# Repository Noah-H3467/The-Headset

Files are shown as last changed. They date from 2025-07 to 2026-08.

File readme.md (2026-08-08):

#  The Headset

"The Headset" is a prototype control system for a wearable headset built around an Arduino Nano Every. The goal is to coordinate physical hardware behavior on the microcontroller at the tap of buttons that are wired to the board, in order to automate the application of a cold compress on the wearer's eyes for the goal of treating eye itching and pain caused by allergies.

I am working on this 'automated allergy icer' because each spring, I repeatedly find myself holding a cold washcloth to my eyes to fight off the pain that comes with my allergies. So my goal was to “automate” the washcloth: I wanted a hands-free way to apply and maintain a cold compress on one or both eyes. The prototype has achieved this key functionality, but is in need of refinement.
- There are currently three buttons. The first two toggle the left and right "arms" up and down. At the end of each arm is a small cold pack attached to it. The third button is an Emergency Stop button, cutting output to the motors.

## Navigation
- This is a PlatformIO project, allowing for easier development in VSCode as opposed to the Arduino IDE.
- The `src` folder contains the code in C++ for the allergy icer. The `include` and `lib` folders may contain other code files in the future as I change the code structure.
- The `CAD` folder contains all cad related things. Parts will contain stl files for 3d printed parts and drawings will contain part and assembly drawings.
- Documentation will contain the initial BOM and an updated one for future iterations, as well as other notes I have made about this project.

## Hardware Control In The Sketch
The C++ source code is structured as a small embedded control loop rather than a collection of one-off callbacks. In `sketch/main.cpp`, the firmware keeps the live hardware state in a few shared variables (arm state, emergency stop enabled) and updates them through handlers called by `checkButtons()`. Those handlers are intentionally lightweight, while the `updateSetpoints()` function, also called by the `periodic()` loop, is responsible for quickly applying that state to the hardware.

The supporting C++ files reinforce the split between main logic and hardware-managing code: 
- Pin mapping and board-specific constants live in `src/Constants.hpp`
- Button handling is wrapped in `DigitalInput` for debouncing and edge detection
- Temperature sensing is isolated in `Thermometer` so the main sketch can treat sensing as a service rather than embedding hardware details inline. 

This way, the firmware can keep safety-sensitive behavior local to the microcontroller and avoid relying on web requests for timing.

Motor control is still in progress, but the architecture already has the intended structure: `main.cpp` computes desired setpoints from the current arm state, and the lower-level DCMotor.hpp consumes those setpoints once it is fully wired up.

## How to Use
- Use the resources in this repository to obtain the materials necessary to build the headset. Either clone this repository or specifically download the STL files to print the custom parts.
 - Note: As the current CAD version is still under refinement, it is not uploaded to the CAD folder yet.
- Download the Arduino IDE and copy the code into a `.ino` file. If you didn't clone the repository, make sure that `TheHeadset.ino` is inside a folder calledd "TheHeadset" to use in the Arduino IDE. 
- Or use the PlatformIO extension in your IDE (like VSCode), clone the repo, and open this Arduino project there.

## Current and Future Plans (in this project's Github Issues)
I intend to make improvements for this prototype and turn it into a refined product. I still intend to stay open source. Future iterations will:
- Use a more compact microcontroller - Arduino Nano Every - and design a custom PCB to lighten the design in order to improve user comfortability.
- Large modifications to the frame to improve appearance and user comfortability.
- Improve consistency of arm subsystems by switching to a different DC motor with a custom-designed gearbox.
- Create a better way of informing the user that a cold pack has warmed: I will likely use LEDs or a buzzer for this purpose.
- Introduce a self-refrigeration mechanism to increase time between cold pack replacing. This enhancement may feature ice cubes or refrigerant.
 - This is a long-term improvement, something to attempt once the others are successfully completed.

## License
This program is free software: you can redistribute it and/or modify it under the terms of the GNU General Public License as published by the Free Software Foundation, either version 3 of the License, or any later version.

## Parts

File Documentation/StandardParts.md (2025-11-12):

# Standard Parts
Will contain links to off-the-shelf or common parts used.

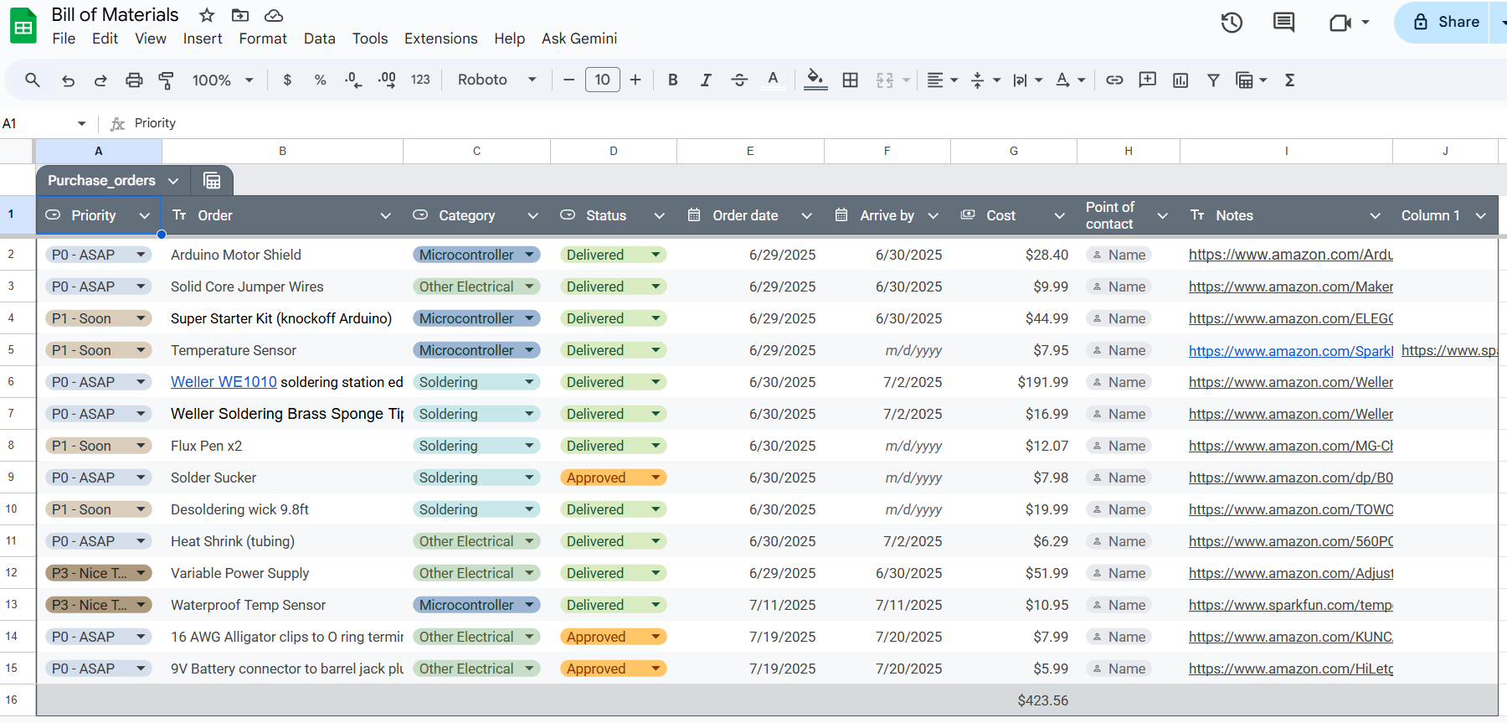
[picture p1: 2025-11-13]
Documentation/Initial Bill of Materials.png

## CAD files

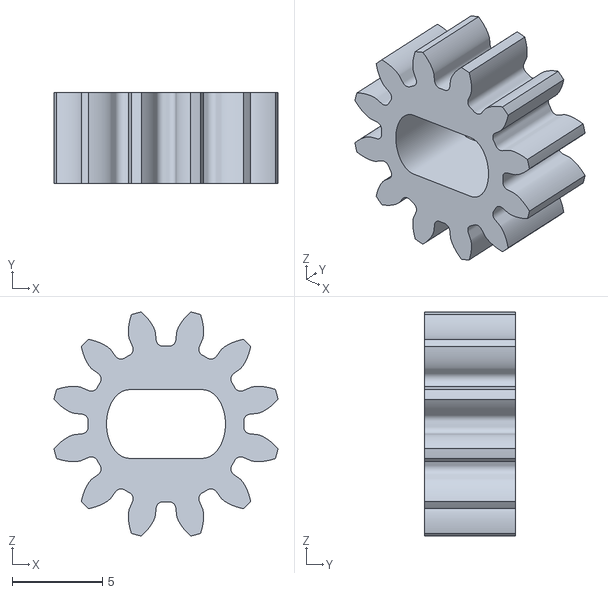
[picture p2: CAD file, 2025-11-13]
CAD/Parts/Gears - Spur gear (12 teeth).stl
12.4 x 5.08 x 12.4

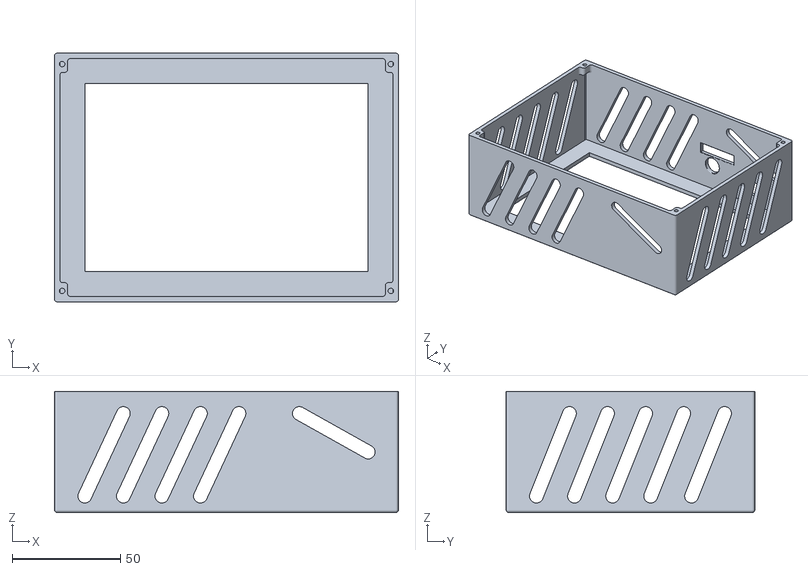
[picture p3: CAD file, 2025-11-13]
CAD/Parts/Controller Housing - Base.stl
158.7 x 114.7 x 55.8

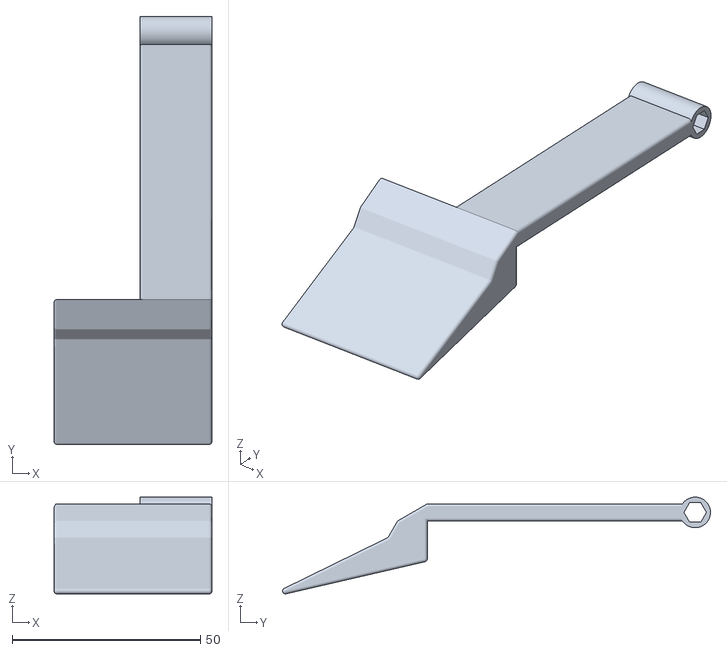
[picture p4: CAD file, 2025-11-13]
CAD/Parts/Arms - Left Arm.stl
41.9 x 113.6 x 25.7

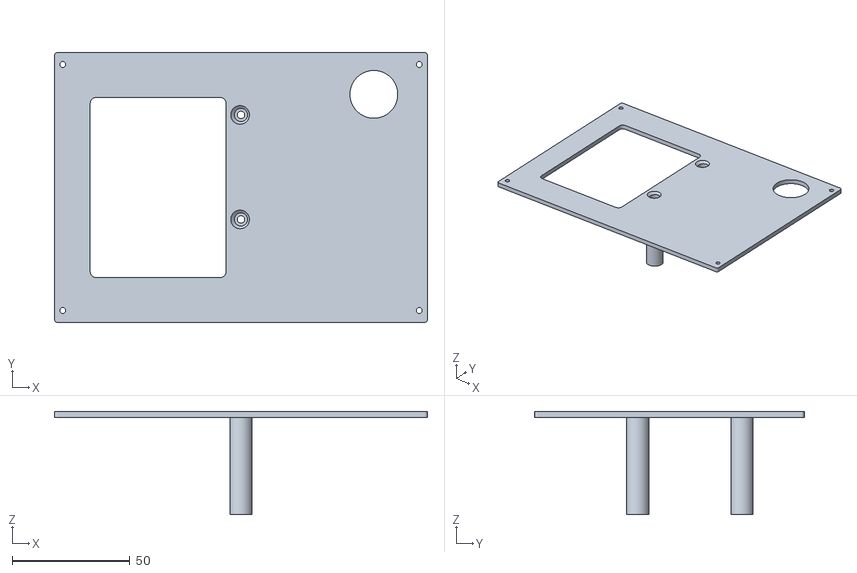
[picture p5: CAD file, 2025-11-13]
CAD/Parts/Controller Housing - Lid.stl
158.7 x 114.7 x 43.9

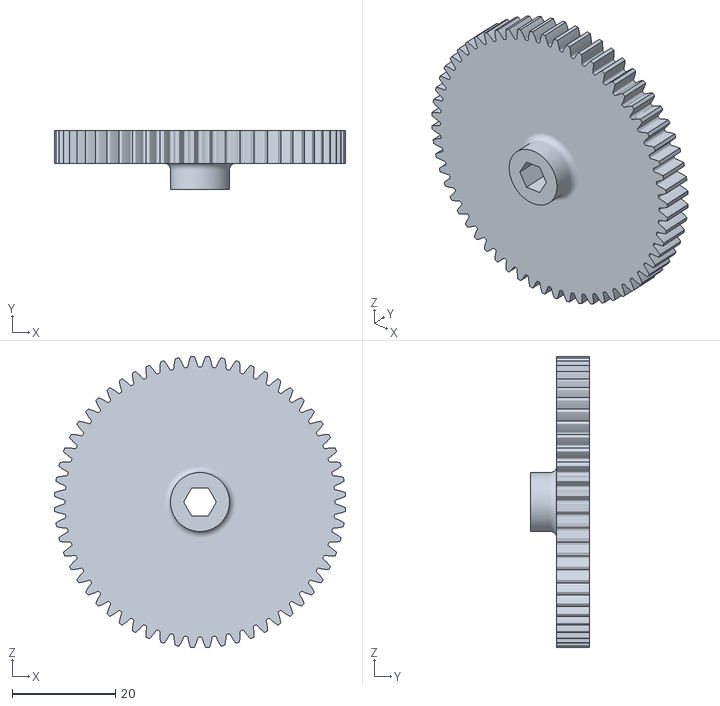
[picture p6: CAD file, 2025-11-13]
CAD/Parts/Gears - Spur gear (60 teeth).stl
56.4 x 11.4 x 56.4

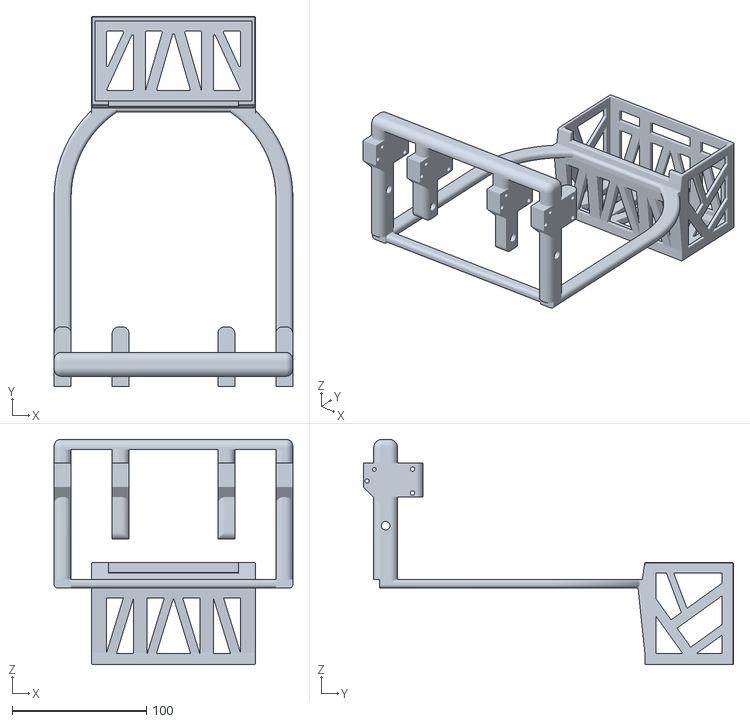
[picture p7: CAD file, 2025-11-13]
CAD/Parts/Headset Frame.stl
177.8 x 275.6 x 167.9

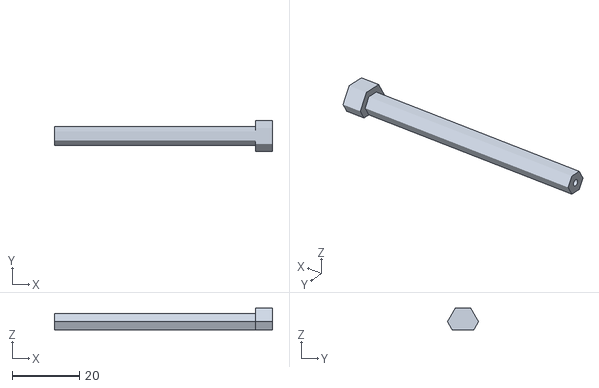
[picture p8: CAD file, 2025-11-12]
CAD/Parts/Axles - Arm Pivot Hex.stl
64.8 x 9.25 x 6.43

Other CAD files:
CAD/Parts/Arms - Right Arm.stl

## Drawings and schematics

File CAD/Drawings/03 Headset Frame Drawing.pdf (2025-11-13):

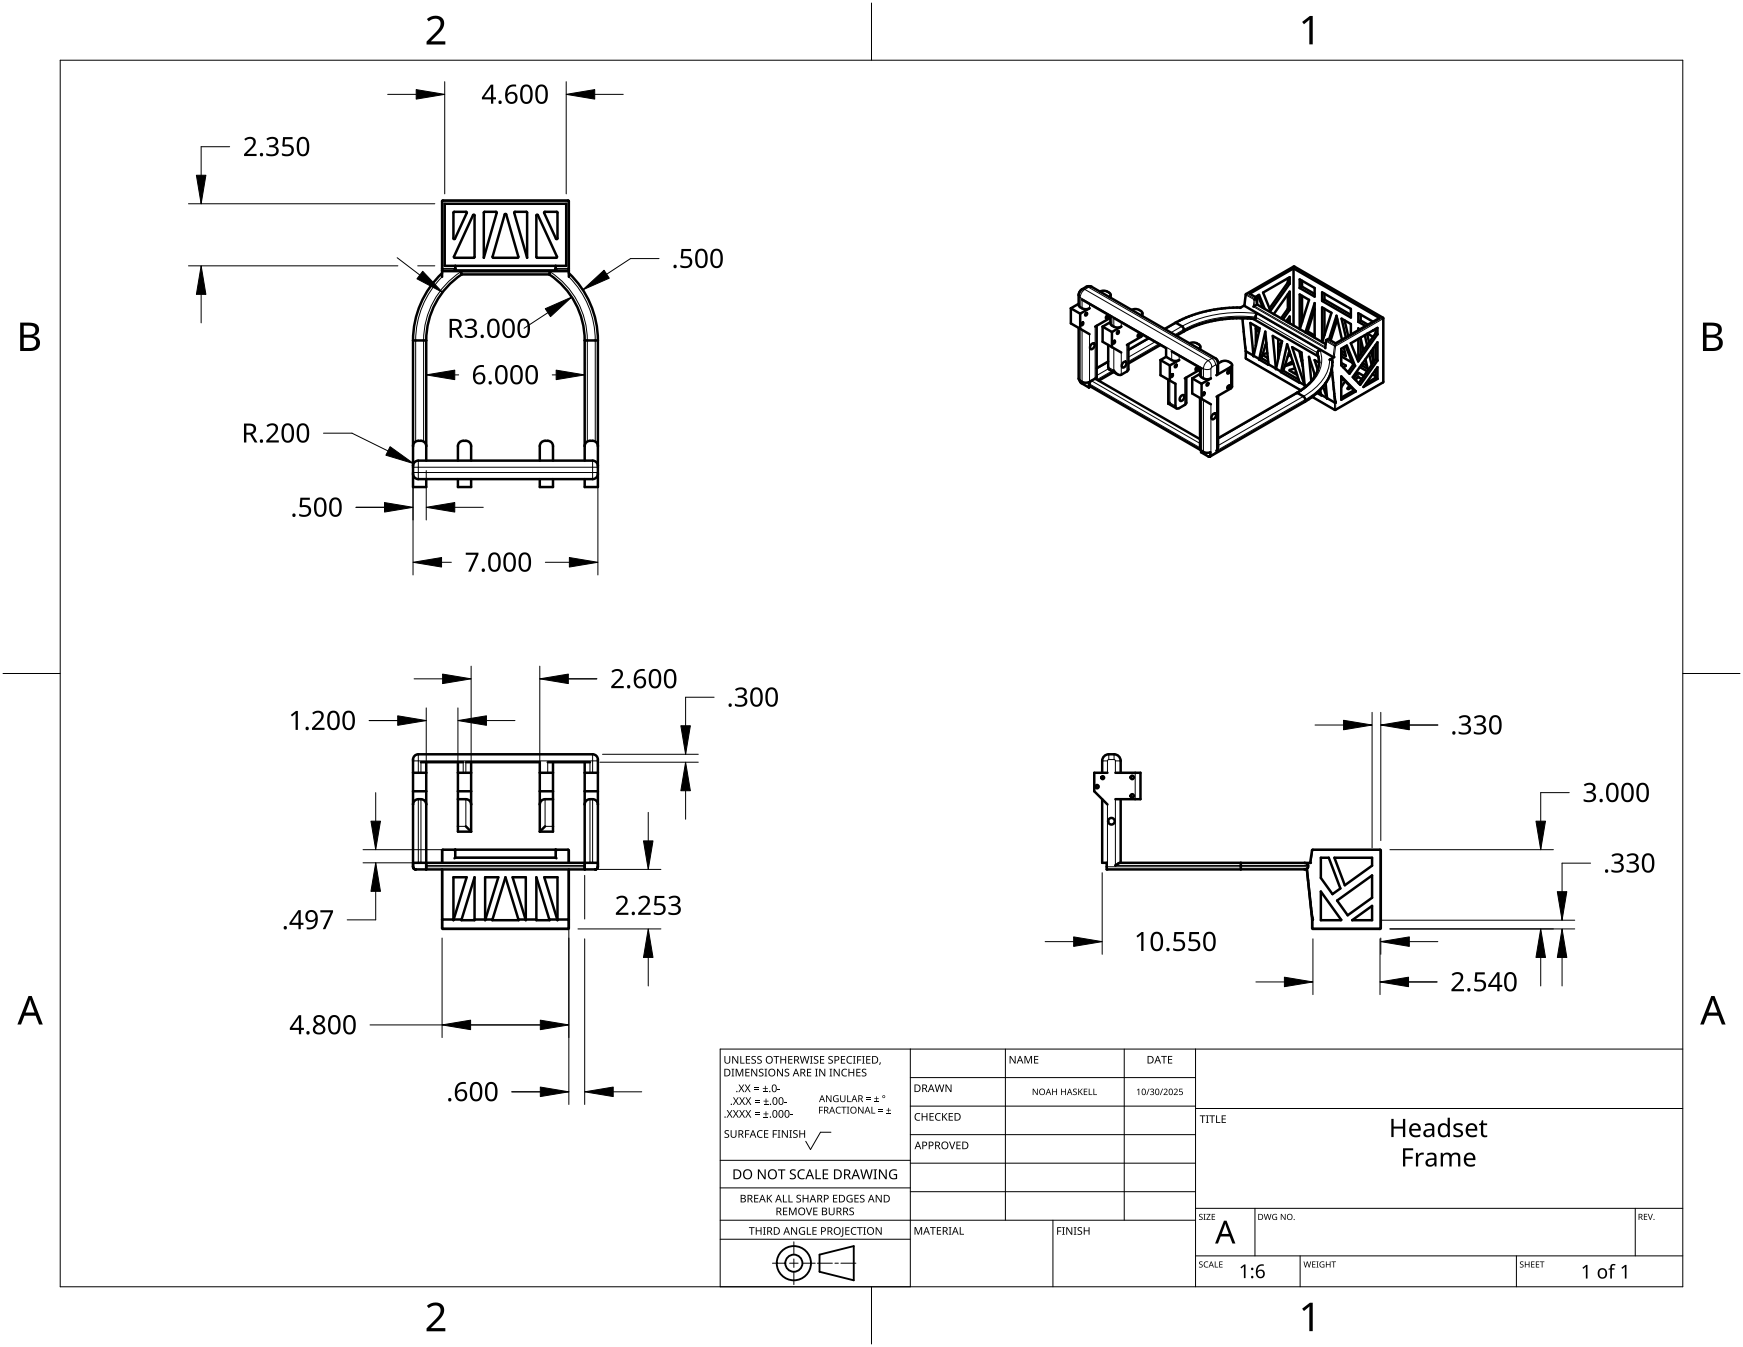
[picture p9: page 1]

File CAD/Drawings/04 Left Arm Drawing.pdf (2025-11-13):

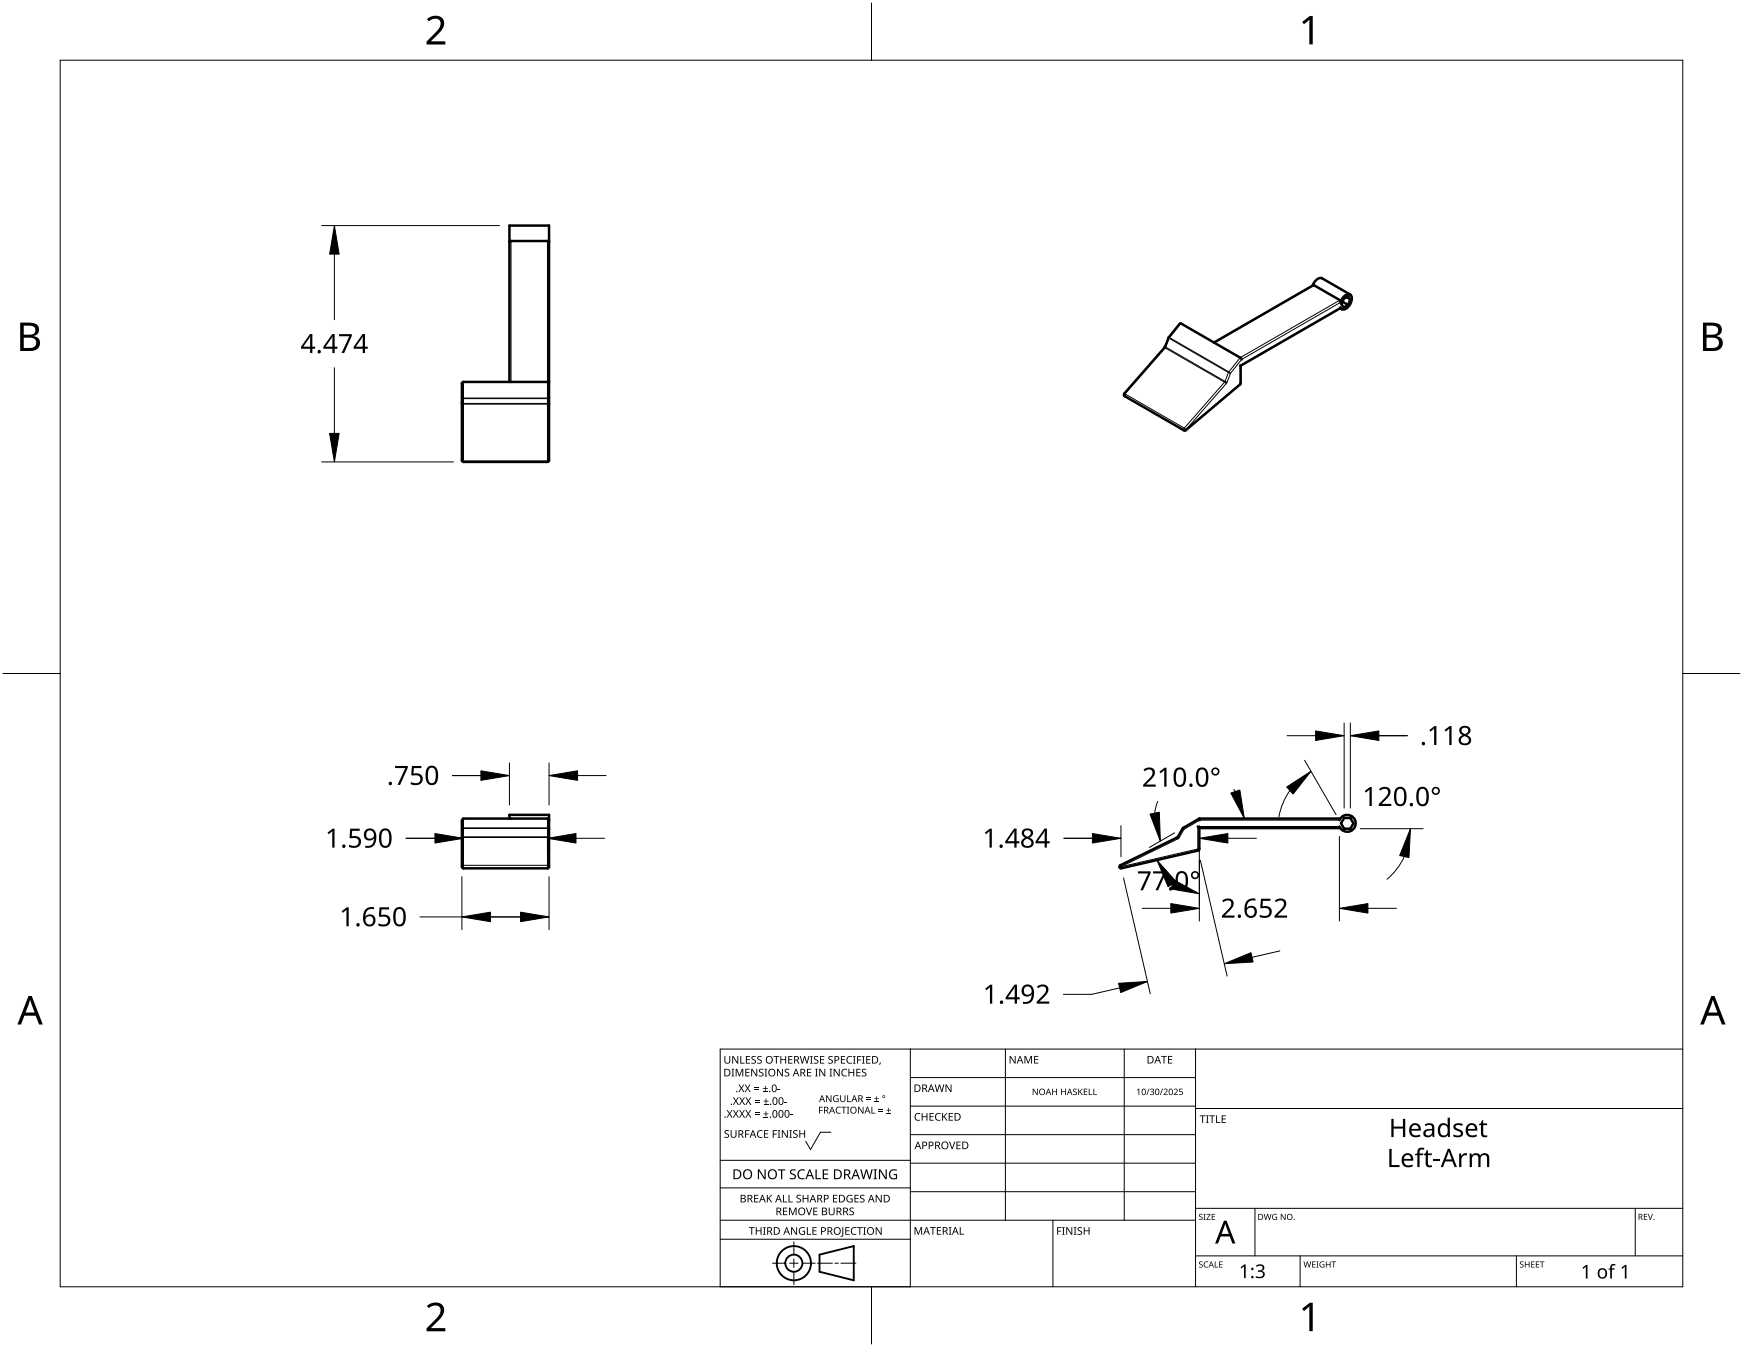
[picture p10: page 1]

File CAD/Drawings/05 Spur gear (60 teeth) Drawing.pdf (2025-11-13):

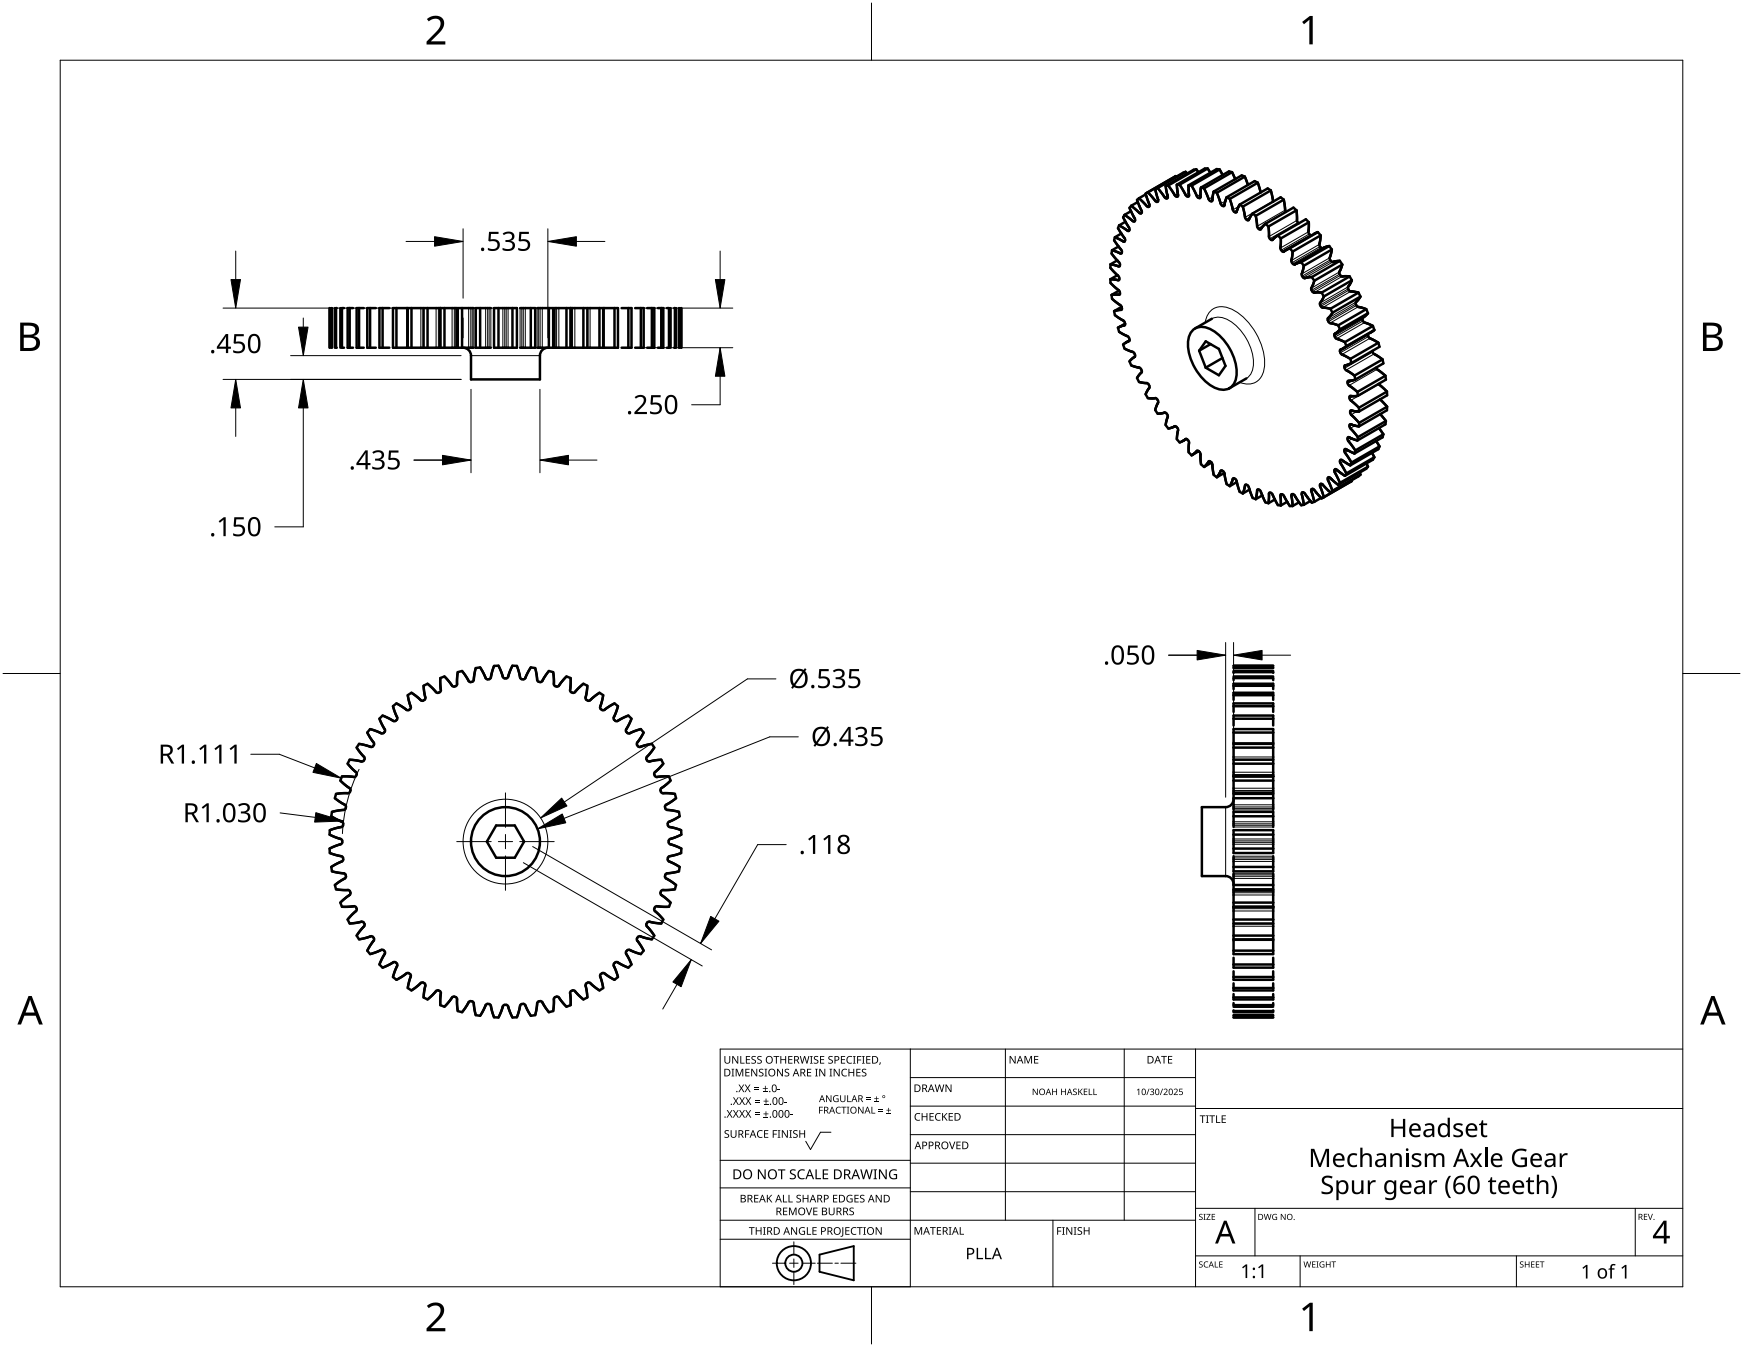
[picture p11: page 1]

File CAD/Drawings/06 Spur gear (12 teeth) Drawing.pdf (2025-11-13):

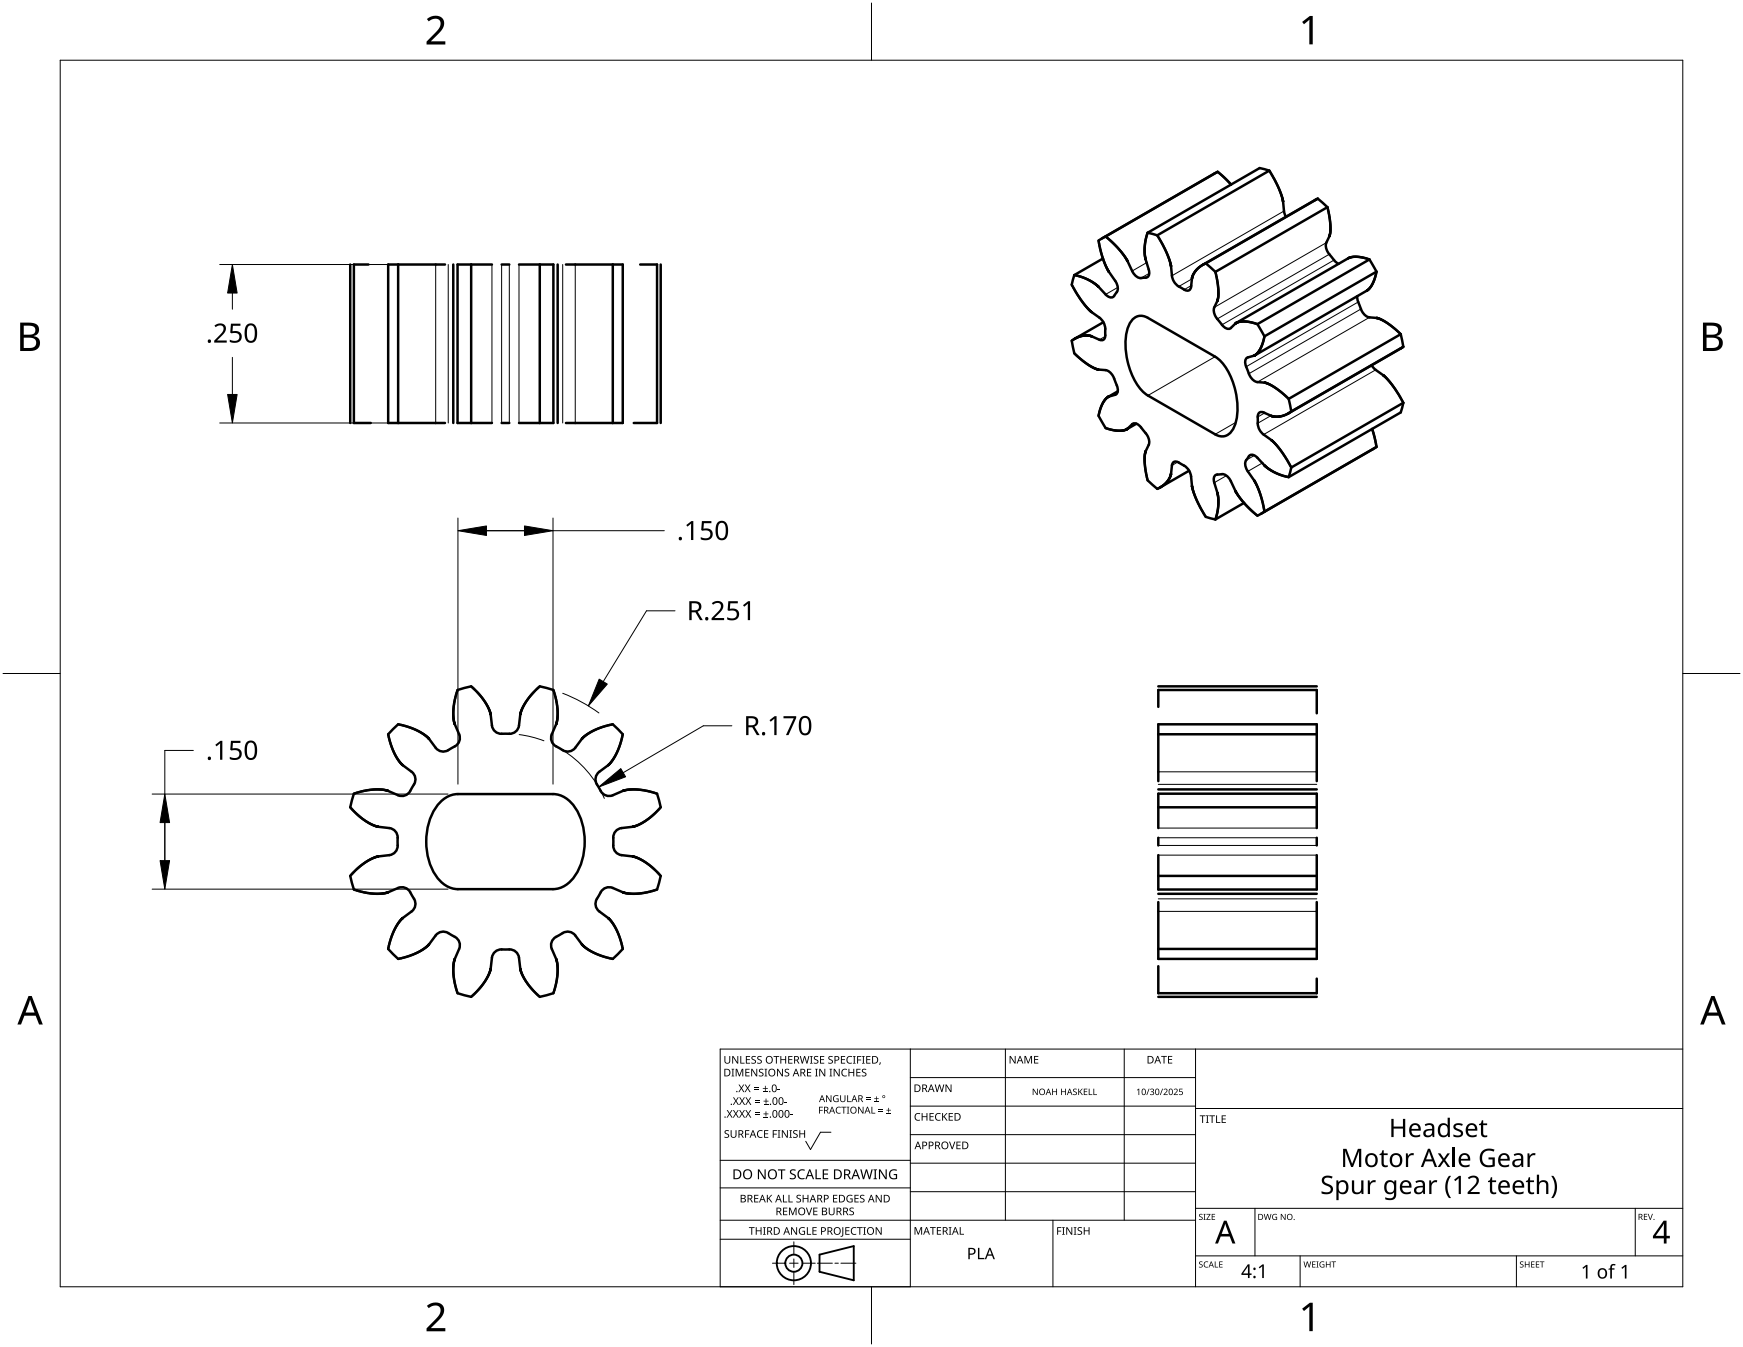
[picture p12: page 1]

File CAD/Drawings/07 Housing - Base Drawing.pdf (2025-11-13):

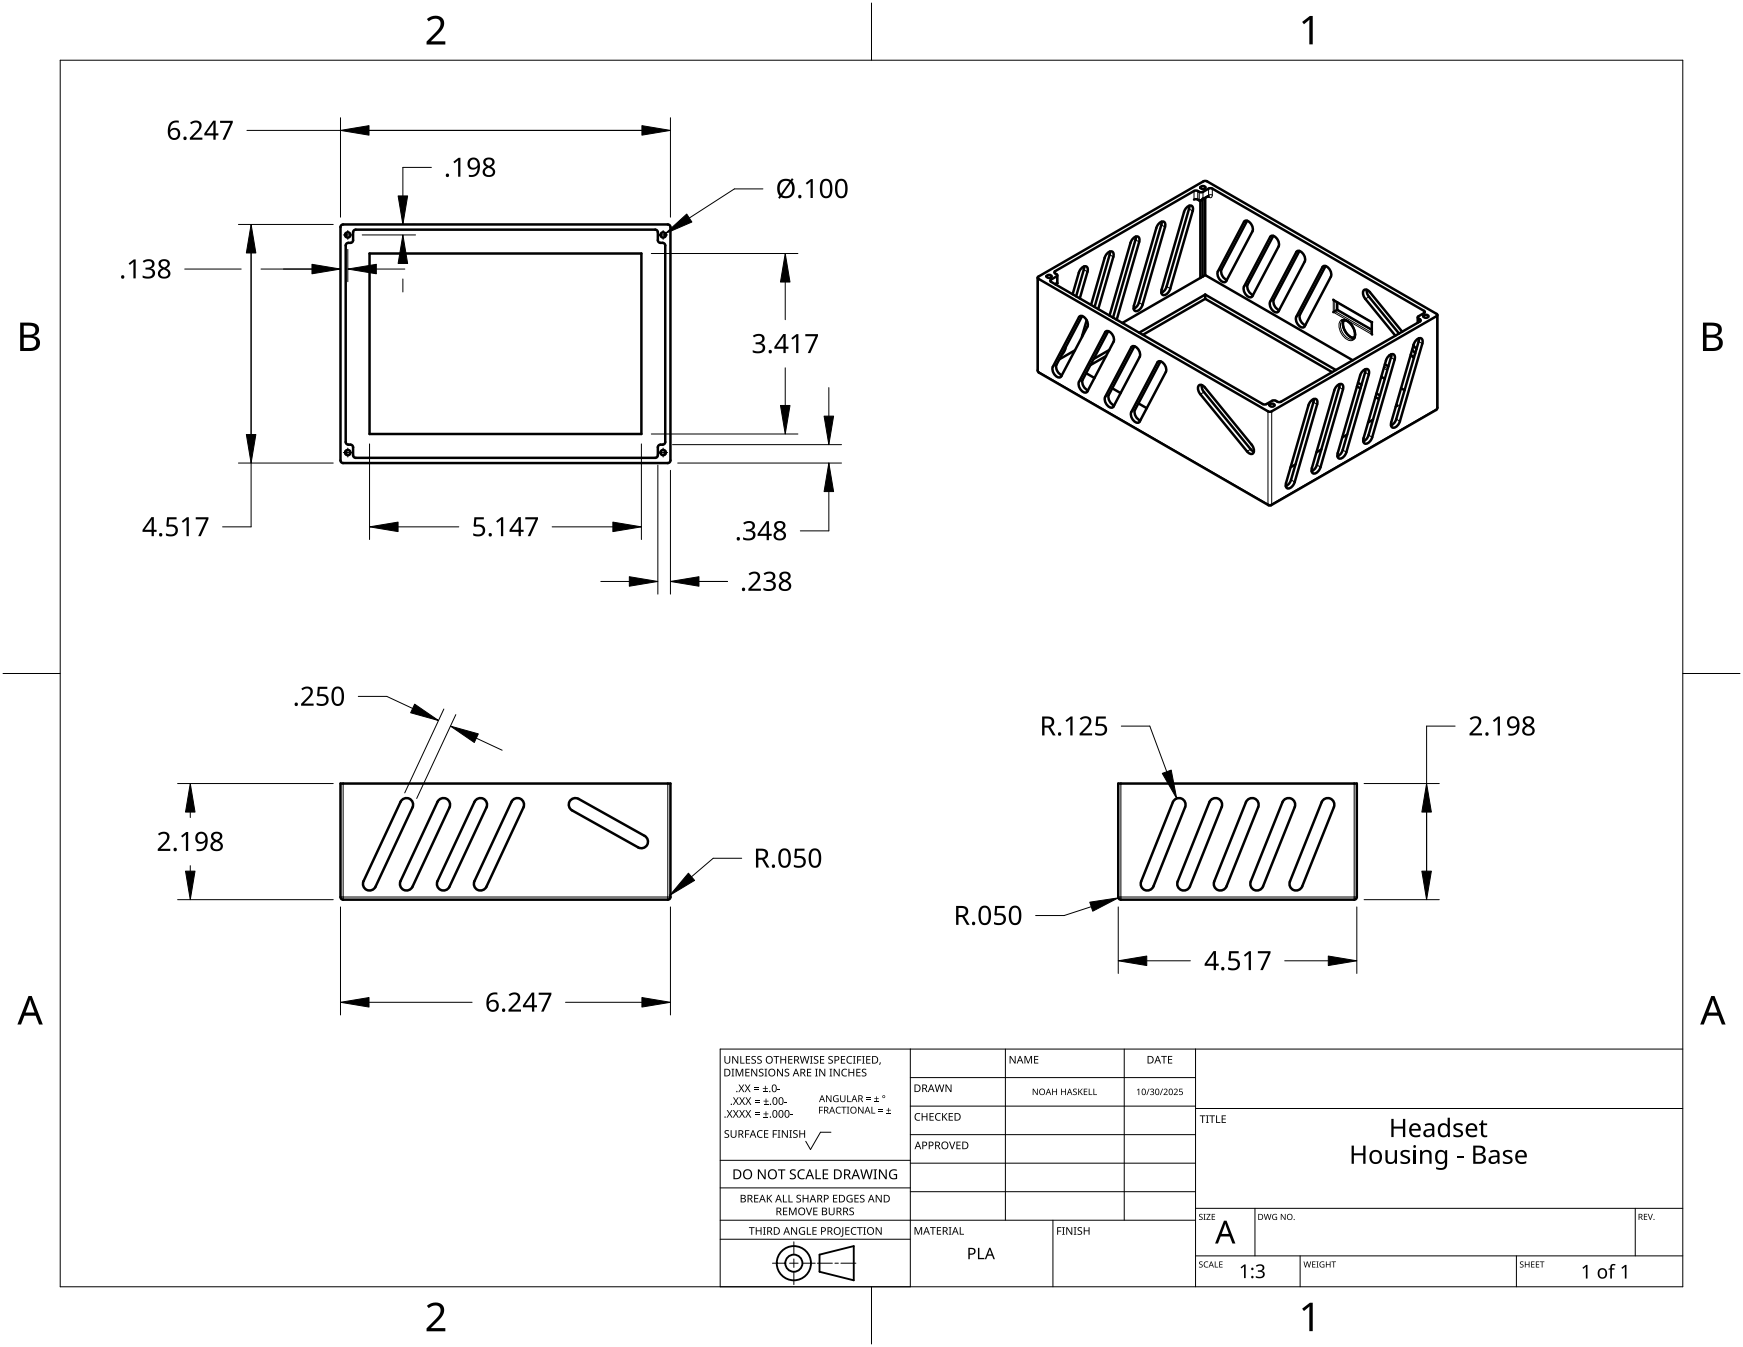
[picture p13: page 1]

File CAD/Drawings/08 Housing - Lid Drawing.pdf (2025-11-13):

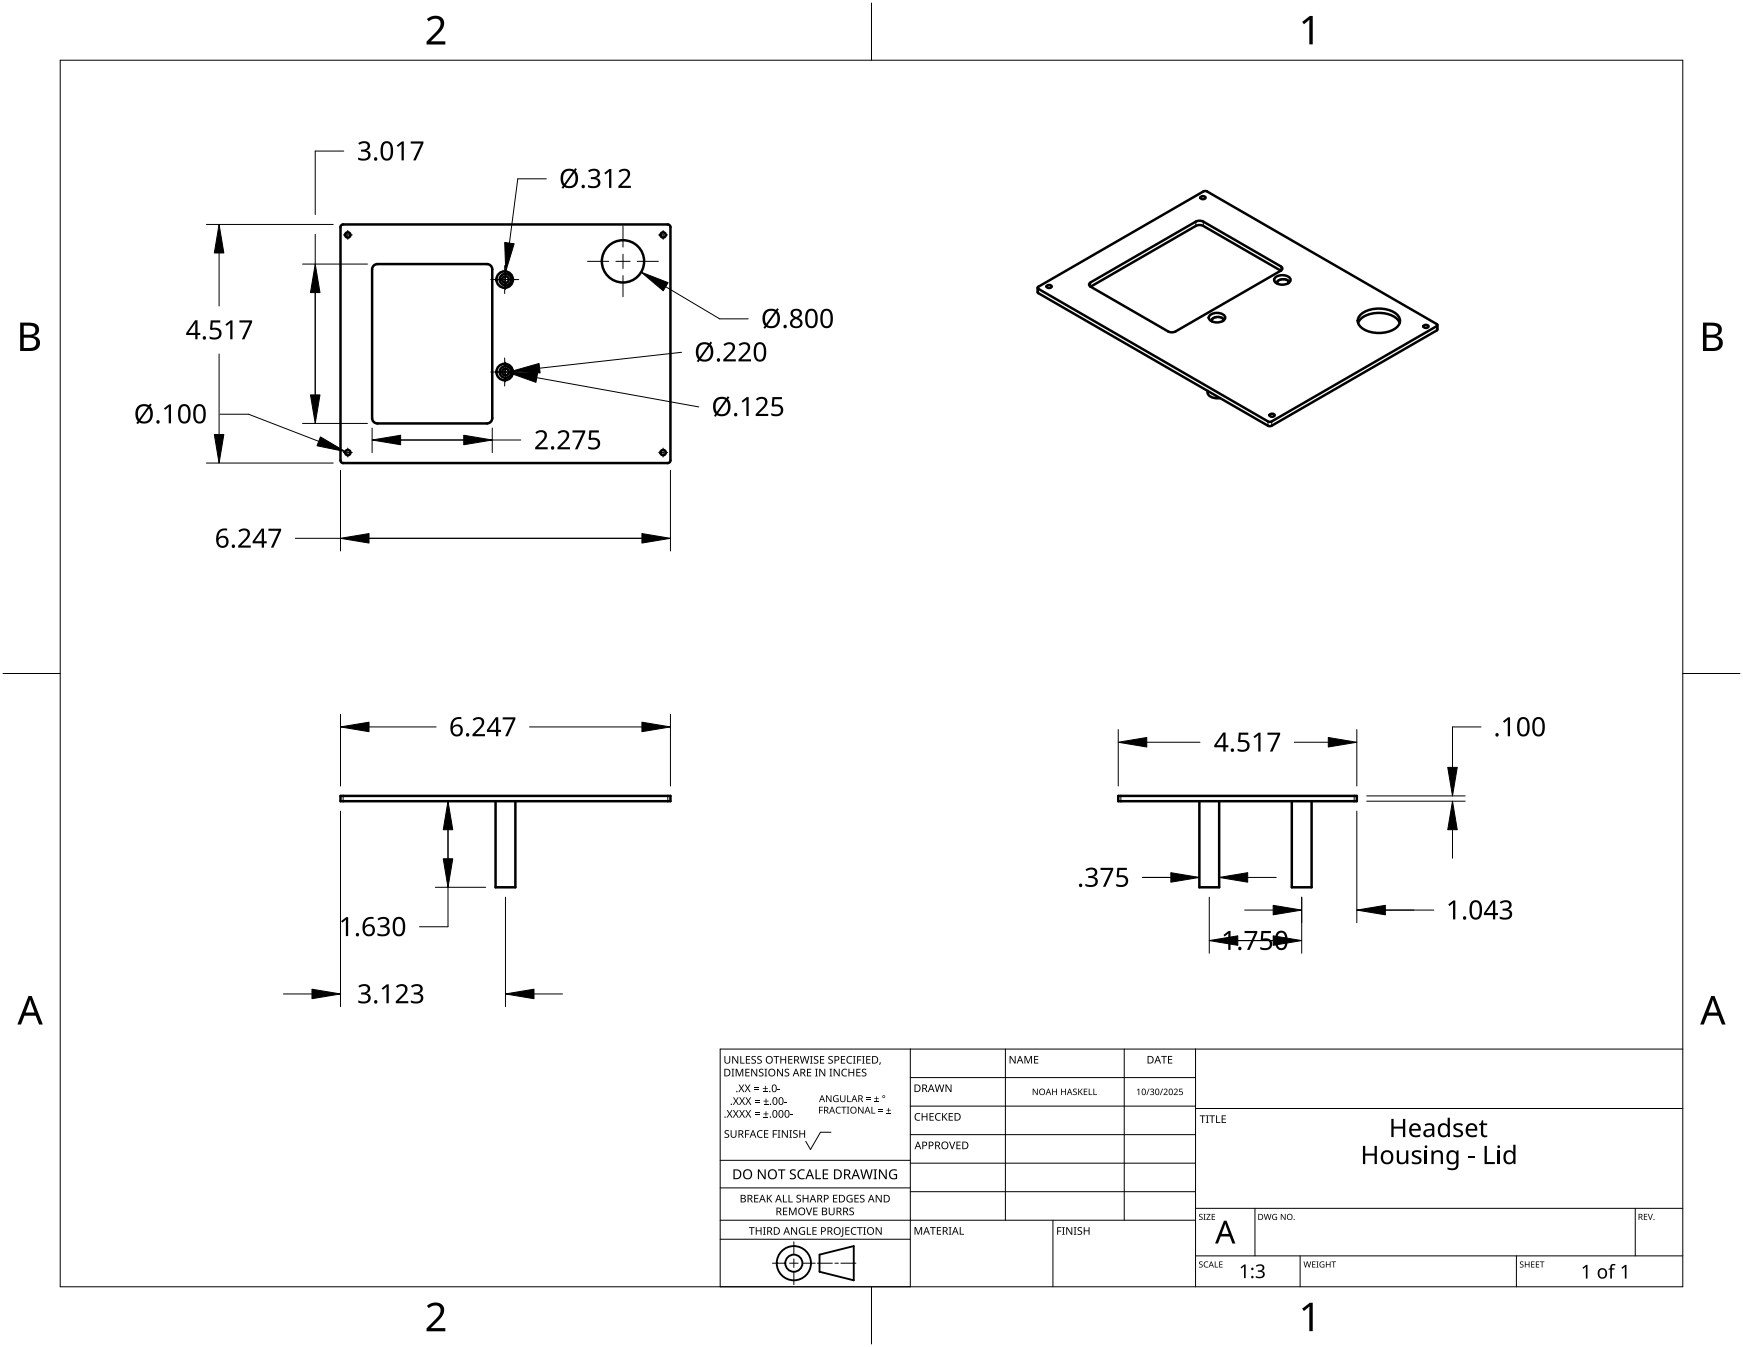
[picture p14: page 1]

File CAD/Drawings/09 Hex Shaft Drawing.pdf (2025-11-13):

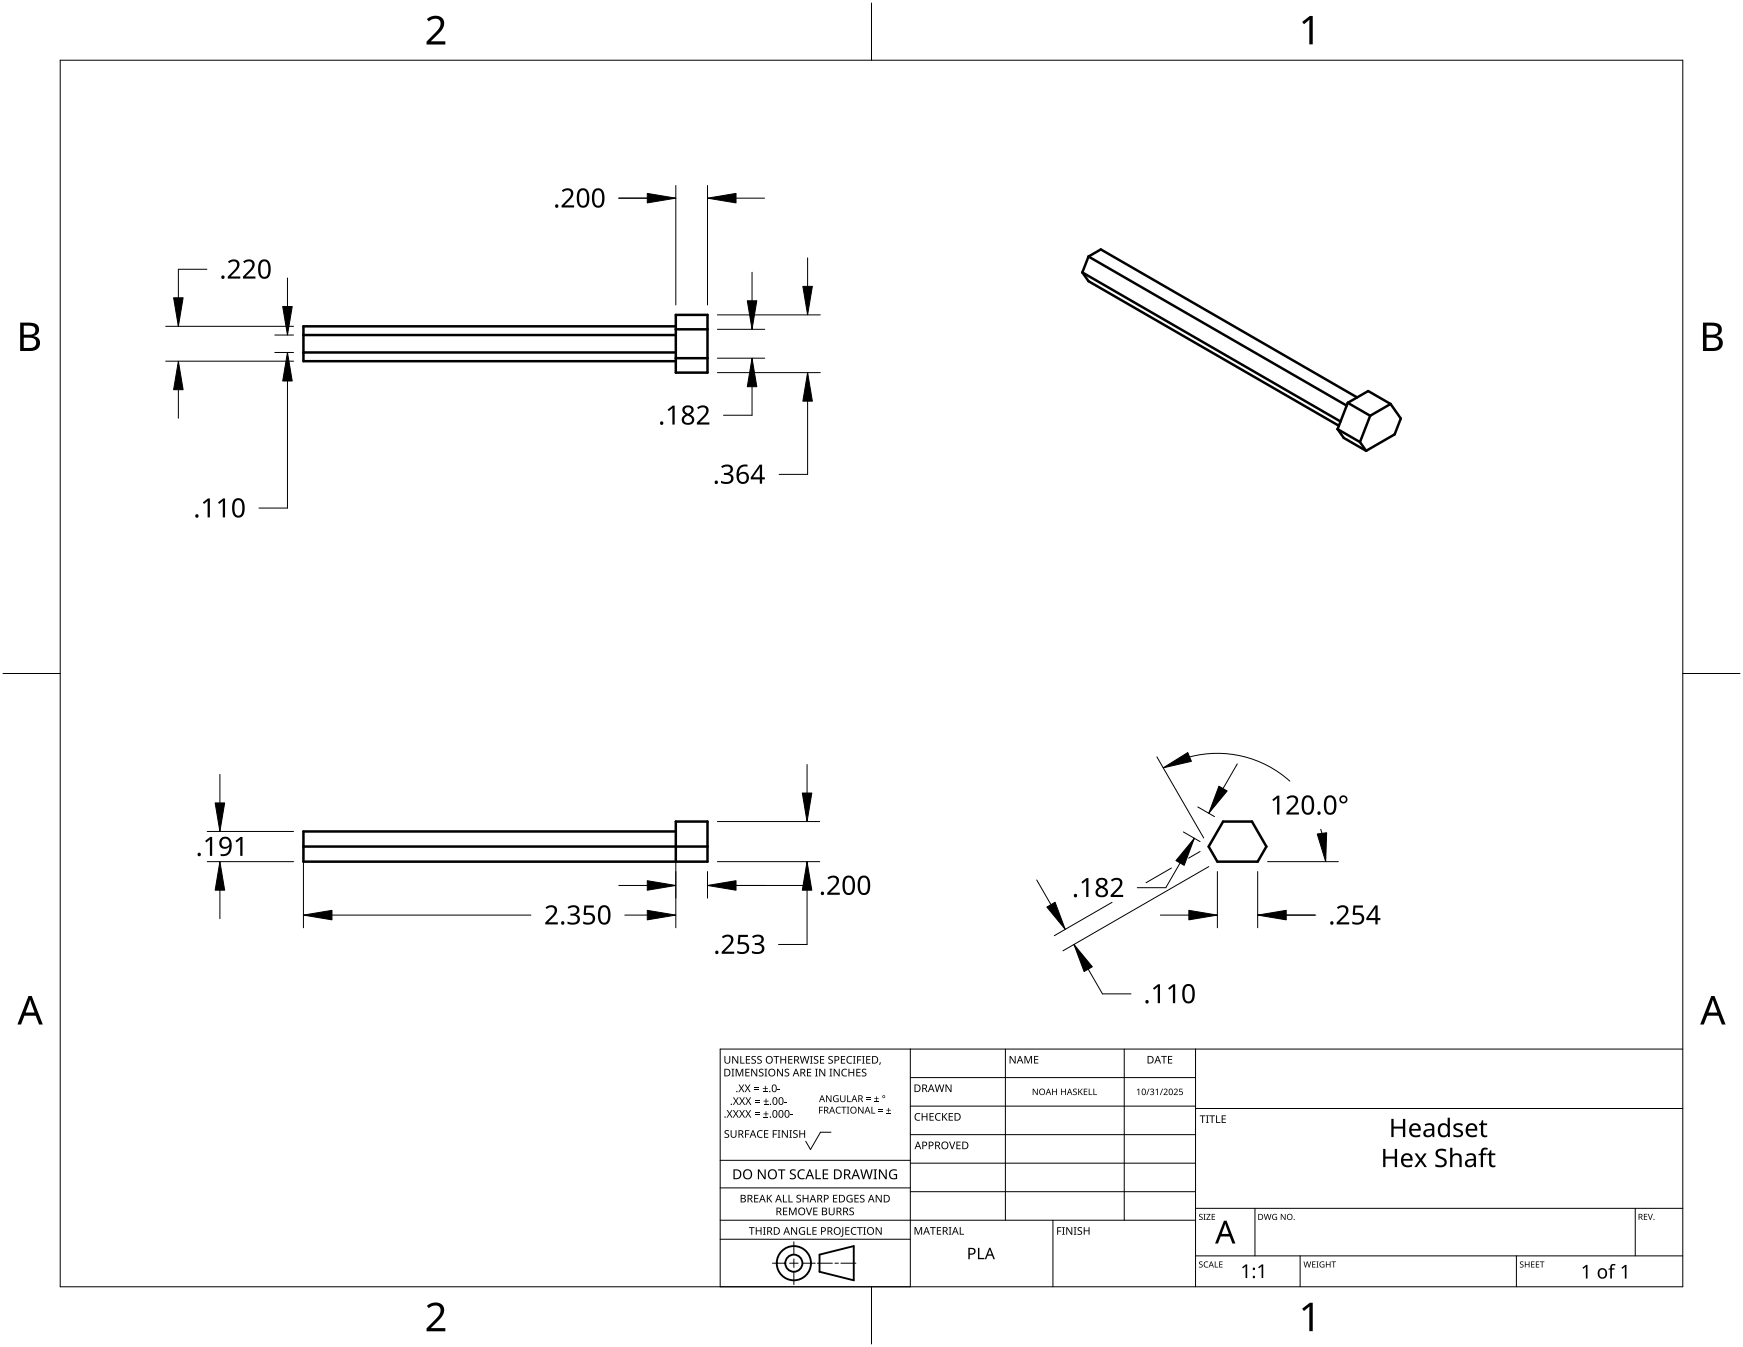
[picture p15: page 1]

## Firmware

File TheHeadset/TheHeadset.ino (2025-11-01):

#include <util/atomic.h>
#include <DallasTemperature.h>
#include <OneWire.h>
#include <QuadratureEncoder.h>

/* Based on a SimplePID class from CurioRes to compute the control signal. 
  I used it out of convenience to familiarize myself with class structure in C++.
  https://github.com/curiores/ArduinoTutorials/blob/main/MultipleEncoders/SimplePositionPID/SimplePositionPID.ino */
class SimplePID{
  private:
    float kp, kd, ki, ks, umax; // Parameters
    float eprev, eintegral; // Storage

  public:
  // Constructor
  SimplePID() : kp(1), kd(0), ki(0), ks(50), umax(255), eprev(0.0), eintegral(0.0){}

  // A function to set the parameters
  void setParams(float kpIn, float kdIn, float kiIn, float ksIn, float umaxIn){
    kp = kpIn; kd = kdIn; ki = kiIn; ks = ksIn; umax = umaxIn;
  }

  // A function to compute the control signal
  void evalu(int value, int target, float deltaT, int &pwr, int &dir){
    // error
    int e = target - value;
  
    // derivative
    float dedt = (e-eprev)/(deltaT);
  
    // integral
    eintegral = eintegral + e*deltaT;

    // control signal
    float u = kp*e + kd*dedt + ki*eintegral;
  
    // motor power
    pwr = (int) fabs(u);
    if( pwr > umax ){
      pwr = umax;
    } else if (pwr < ks) {
      pwr = ks;
    }
  
    // motor direction
    dir = 1;
    if(u>0){
      dir = -1;
    }
  
    // store previous error
    eprev = e;
  }
};

// Define Sensors
#define ONE_WIRE_BUS 4 // Pin # of Sensor 1
#define TWO_WIRE_BUS 10 // Pin # of Sensor 2
OneWire oneWire(ONE_WIRE_BUS);
OneWire twoWire(TWO_WIRE_BUS);
DallasTemperature sensor1(&oneWire); // Left
DallasTemperature sensor2(&twoWire); // Right

// {Right Motor, Left Motor}
const int DIRECTION_PINS[] = {12, 13};
const int PWM_PINS[] = {3, 11};
const int BRAKE_PINS[] = {9, 8};
Encoders firstEncoder(2,5);
Encoders secondEncoder(6,7); // the encoder objects could use analog pins

//boolean to switch motor direction
bool directionState = false;

// Initial target position
const int highPos = 800;
const int lowPos = -50;
int target[] = {highPos, highPos};

// For PID time calculation
long prevT = 0;

// PID class instance list length 2 - number of motors
SimplePID pid[2];
int STATIC_GAIN[] = {255, 73}; // for each motor

// Counter for printing position on the serial
int counter = 0;

// Define button pins
// https://forum.arduino.cc/t/using-analog-pins-for-push-buttons/309407/7
const int leftButton = A0;
const int rightButton = A1;
// Press this to zero the encoders. TODO: Make the press of this button start homing
const int homeButton = A2;
// Records the button state. Either HIGH or LOW.
int leftButtonState = LOW;
int rightButtonState = LOW;
bool homeButtonState = LOW;

void setup() {
  Serial.begin(9600);
  sensor1.begin();
  sensor2.begin();
  
  //define pins
  for (int k = 0; k < 2; k++) {
    // MOTOR
    pinMode(DIRECTION_PINS[k], OUTPUT);
    pinMode(PWM_PINS[k], OUTPUT);
    pinMode(BRAKE_PINS[k], OUTPUT);

    pid[k].setParams(3,0.15,0.0,50,255);
  }

  resetEncoders();
  // Tell Motor #1 to stop
  setMotor(1, DIRECTION_PINS[0], 0.0, PWM_PINS[0]);

  // Initialize the button pins as inputs:
  pinMode(leftButton, INPUT);   
  pinMode(rightButton, INPUT);
  pinMode(homeButton, INPUT);
}

unsigned long lastMilli = 0;
unsigned long lastTempMilli = 0; // To be able to run long temperature stuff that takes a second while checking PID
unsigned long lastTempInProgressMilli = 0;

void loop() {

  /* Request and report temperature ever 30 sec */
  if (millis()-lastTempMilli >= 30000) {
    lastTempMilli = millis();
    requestTemps();
    lastTempInProgressMilli = millis();

    while (millis()-lastTempInProgressMilli < 750) {
      if (millis()-lastMilli > 20) {
        lastMilli = millis();  

        updateButtonState();
        updatePID();
      }
    }
    updateTemperatures();
  }
  if (millis()-lastMilli > 20) {
    lastMilli = millis();  

    updateButtonState();
    updatePID();

  }
}

void requestTemps() {
  // Get temperatures
  sensor1.requestTemperatures();
  sensor2.requestTemperatures();
}

// requestTemps() must be called at least 0.75 seconds before calling this
// Currently gets thermometer reading and prints it to the serial.
void updateTemperatures() {
  Serial.print("Sensor 1: Celsius temperature: ");
  // Why "byIndex"? One can have more than one IC on the same bus. 0 refers to the first IC on the wire
  Serial.print(sensor1.getTempCByIndex(0)); 
  Serial.print(" - Fahrenheit temperature: ");
  Serial.println(sensor1.getTempFByIndex(0));
  Serial.print("Sensor 2: Celsius temperature: ");
  Serial.print(sensor2.getTempCByIndex(0)); 
  Serial.print(" - Fahrenheit temperature: ");
  Serial.println(sensor2.getTempFByIndex(0));

  delay(1000); // Update every second
}

void updatePID() {

  // time difference
  long currT = micros();
  float deltaT = ((float) (currT - prevT))/( 1.0e6 );
  prevT = currT;
  
  lastMilli = millis();  

  long pos[2];
  pos[0] = -firstEncoder.getEncoderCount();
  pos[1] = secondEncoder.getEncoderCount();

  // loop through the motors
  for(int k = 0; k < 2; k++){
    int pwr, dir;
    // evaluate the control signal
    pid[k].evalu(pos[k], target[k], deltaT, pwr, dir);
    // signal the motor
    // Flip direction for Right Arm motor aka the 1st motor
    if (k==0){
      dir *= -1;
      setMotor(dir, DIRECTION_PINS[k], pwr, PWM_PINS[k]);
    } else {
      setMotor(dir, DIRECTION_PINS[k], pwr, PWM_PINS[k]);
    }
  }
  // Print arm information every 10x this function is called
  if (counter % 10 == 0) {
    for(int k = 0; k < 2; k++){
      if (k == 1) {
      Serial.print("                                                     ");
      }
      Serial.print("Target of motor ");
      Serial.print(k+1);
      Serial.print(": ");
      Serial.print(target[k]);
      Serial.print(" ");
      Serial.print("Position of encoder: ");
      Serial.print(pos[k]);
      Serial.println(" ");
    }
  }
  counter++;
}

void resetEncoders() {
  // Through testing, -20 ticks has been more effective than 0
  firstEncoder.setEncoderCount(-20.0);
  secondEncoder.setEncoderCount(-20.0);
}

void setMotor(int dir, int dirPin, int pwmVal, int pwmPin) {
  if (dir==1) {
    digitalWrite(dirPin, HIGH);
    //set work duty for the motor
    analogWrite(pwmPin, pwmVal);
  } else if (dir == -1) {
    digitalWrite(dirPin, LOW);
    //set work duty for the motor
    analogWrite(pwmPin, pwmVal);
  } else {
    analogWrite(pwmPin, 0);
  }
}

void updateButtonState() {
  // Checks to see if the new reading is the same as the existing state
  if (leftButtonState != digitalRead(leftButton)) {
    // If not, Update to the leftButtonState
    leftButtonState = digitalRead(leftButton);
    if (leftButtonState == HIGH) {
      // If the button was just pressed, toggle the target position
      if (target[0] == highPos) {
        target[0] = lowPos;
      } else {
        target[0] = highPos;
      }
    }
  }

  // Checks to see if the new reading is the same as the existing state
  if (rightButtonState != digitalRead(rightButton)) {
    // If not, Update to the rightButtonState
    rightButtonState = digitalRead(rightButton);
    if (rightButtonState == HIGH) {
      // If the button was just pressed, toggle the target position
      if (target[1] == highPos) {
        target[1] = lowPos;
      } else {
        target[1] = highPos;
      }
    }
  }
  
  // Zero the motor encoders right when home button is pressed
  if (homeButtonState != digitalRead(homeButton)) {
    homeButtonState = digitalRead(homeButton);
    if (homeButtonState == HIGH) {
      resetEncoders();
    }
  }
}

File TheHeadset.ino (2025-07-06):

#include <OneWire.h>
#include <DallasTemperature.h>

// Define Sensors
#define ONE_WIRE_BUS 2 // Pin # of Sensor 1
#define TWO_WIRE_BUS 10 // Pin # of Sensor 2
OneWire oneWire(ONE_WIRE_BUS);
OneWire twoWire(TWO_WIRE_BUS);
DallasTemperature sensor1(&oneWire);
DallasTemperature sensor2(&twoWire);

// Serial
// SoftwareSerial display(3, 2);

// Motor #1
int directionPin = 12;
int pwmPin = 3;
int brakePin = 9;
// Encoder #1
#define ENCODER_1A 4 // Yellow on shield, white on motor
#define ENCODER_1B 5 // White on shield, green on motor

//uncomment if using channel B, and remove above definitions
//int directionPin = 13;
//int pwmPin = 11;
//int brakePin = 8;
// Encoder #2
// #define ENCODER_2A = 6;
// #define ENCODER_2B = 7;

//boolean to switch motor direction
bool directionState = false;

// Position of each motor
int posOne = 0;
int posTwo = 0;
// Target position
int target = 100;

void setup() {
  Serial.begin(9600);
  sensor1.begin();
  sensor2.begin();
  
  //define pins
  // Motor + Encoder #1
  pinMode(directionPin, OUTPUT);
  pinMode(pwmPin, OUTPUT);
  pinMode(brakePin, OUTPUT);
  pinMode(ENCODER_1A,INPUT);
  pinMode(ENCODER_1B, INPUT);
  // Interrupts whenever ENCODER_1A rises.
  // readEncoder is the function that should be called when interrupted
  attachInterrupt(digitalPinToInterrupt(ENCODER_1A),readEncoder,RISING);
  // analogWrite(pwmPin, 100);
  
}


void loop() {
  // Currently gets thermometer reading and prints it to the serial.
  // updateTemperatures();
  updatePID();

  /*
  //change direction every loop()
  directionState = !directionState;

  //write a low state to the direction pin (13)
  if(directionState == false){
    digitalWrite(directionPin, LOW);
  }

  //write a high state to the direction pin (13)
  else{
    digitalWrite(directionPin, HIGH);
  }

  //release breaks
  digitalWrite(brakePin, LOW);

  //set work duty for the motor
  analogWrite(pwmPin, 100);

  delay(2000);

  //activate breaks
  digitalWrite(brakePin, HIGH);

  //set work duty for the motor to 0 (off)
  analogWrite(pwmPin, 0);

  delay(2000); // */

}

void updateTemperatures() {
  // Get and print temperature
  sensor1.requestTemperatures();
  sensor2.requestTemperatures();
  delay(750);
  //if (temperatureC != DEVICE_DISCONNECTED_C) {
  Serial.print("Sensor 1: Celsius temperature: ");
  // Why "byIndex"? You can have more than one IC on the same bus. 0 refers to the first IC on the wire
  Serial.print(sensor1.getTempCByIndex(0)); 
  Serial.print(" - Fahrenheit temperature: ");
  Serial.println(sensor1.getTempFByIndex(0));
  Serial.print("Sensor 2: Celsius temperature: ");
  // Why "byIndex"? You can have more than one IC on the same bus. 0 refers to the first IC on the wire
  Serial.print(sensor2.getTempCByIndex(0)); 
  Serial.print(" - Fahrenheit temperature: ");
  Serial.println(sensor2.getTempFByIndex(0));
  // } else {
  //  Serial.println("Error: Could not read temperature");
  //}
  delay(1000); // Update every second
}

void updatePID() {

  Serial.print("Position of 1st encoder: ");
  Serial.println(posOne);
  int error = target - posOne;
  if (error > 0) {
    if (error > 100) {
      error = 100;
    }
    setMotor(1, error, pwmPin);
  } else if (error < 0) {
    if (error < -100) {
      error = -100;
    }
    setMotor(-1, error, pwmPin);
  } else {
    setMotor(0, 0, pwmPin);
  }
}

// Called when encoder1A changes state
void readEncoder() {
  Serial.println("readEncoder called");
  delay(500);
  int oneB = digitalRead(ENCODER_1B);
  if (oneB > 0) {
    posOne++;
  } else {
    posOne--;
  }
}

// Called when encoder2A changes state
void readEncoderTwo() {
  // int twoB = digitalRead(ENCODER_2B);
  int twoB = 0;
  if (twoB > 0) {
    posTwo++;
  } else {
    posTwo--;
  }
}

void setMotor(int dir, int pwmVal, int pwm) {
  analogWrite(pwm, pwmVal);
  if (dir==1) {
    digitalWrite(directionPin, HIGH);
  } else if (dir == -1) {
    digitalWrite(directionPin, LOW);
  } else {
    analogWrite(pwm, 0);
  }
}

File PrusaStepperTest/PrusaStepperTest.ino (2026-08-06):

// Basic NEMA 17 Stepper + TMC2209 test - does not implement AccelStepper yet

// Pin Definitions
#define EN_PIN 8    // LOW: Driver enabled, HIGH: Driver disabled
#define STEP_PIN 9  // Step on the rising edge
#define DIR_PIN 10  // Set stepping direction
int noOfSteps = 1500;           // Number of steps to move in each direction
int microSecondsDelay = 1000; // at 12V, 575 us (nearly 2x speed) at 16V; // Delay in microseconds between each step

void setup() {
  // Configure pin modes
  pinMode(EN_PIN, OUTPUT);
  pinMode(STEP_PIN, OUTPUT);
  pinMode(DIR_PIN, OUTPUT);
  // Initialize pin states
  digitalWrite(EN_PIN, LOW);   // Enable the driver
  digitalWrite(DIR_PIN, LOW);  // Set initial direction
  Serial.begin(9600);
}
void loop() {
    // Move motor in one direction
    digitalWrite(DIR_PIN, LOW);  // Set direction to LOW
    Serial.println("LOW");
    moveSteps(noOfSteps);
    // Move motor in the opposite direction
    digitalWrite(DIR_PIN, HIGH); // Set direction to HIGH
    Serial.println("HIGH");
    moveSteps(noOfSteps);
}

void moveSteps(int steps) {
  for (int i = 0; i < steps; i++) {
    digitalWrite(STEP_PIN, HIGH);
    delayMicroseconds(microSecondsDelay);
    digitalWrite(STEP_PIN, LOW);
    delayMicroseconds(microSecondsDelay);
  }
}

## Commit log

2025-07-08 Encoder #1 works, encoder #2 works poorly, motor position control in progress
2025-09-07 Add zeroing button, integrate temperature reporting into periodic structure
2025-10-18 Successful tuning with new gear ratio
2025-11-13 Upload CAD files
    [Arms - Left Arm.stl, Controller Housing - Base.stl, Controller Housing - Lid.stl, Gears - Spur gear (12 teeth).stl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]
